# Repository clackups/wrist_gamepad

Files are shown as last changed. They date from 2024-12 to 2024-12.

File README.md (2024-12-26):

# Wrist controlled gamepad

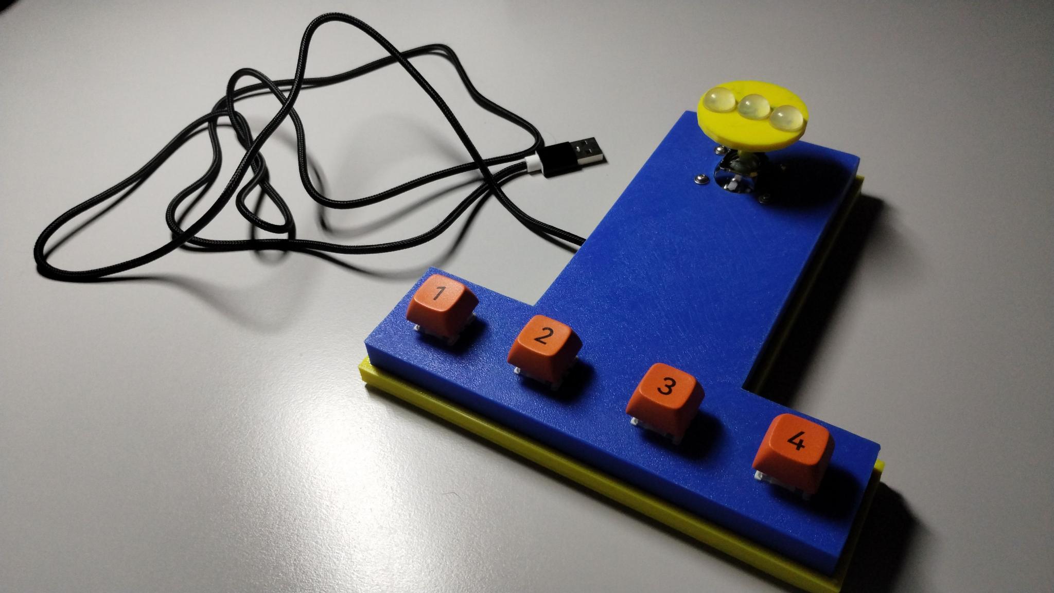
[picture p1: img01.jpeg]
gamepad top view


This is a gamepad I designed for a disabled colleague who cannot bend
his fingers due to a spinal cord injury. The analog joystick is easy to
move with the fingertips, and four buttons can be pressed by the
wrist.

The gamepad runs a copy of [GP2040-CE
firmware](https://gp2040-ce.info/) on an RP2040-Zero board. The four
buttons are wired to GPIO that are mapped by default to buttons
B1..B4, and the joystick push button is mapped to A1. The mapping can
be changed easily in the GP2040 firmware cofiguration. See the
[schematics](wrist_gamepad_schematics.pdf) for reference.

On the bottom of the gamepad, a push-button is wired to the S2
signal. If you press and hold it and plug the USB connector in your
PC, the gamepad starts in configuration mode. You can change the
settings in a browser connected to
[http://192.168.7.1/](http://192.168.7.1/). See the [GP2040
documentation](https://gp2040-ce.info/web-configurator/) for more
details.

The top and bottom parts, as well as the joystick handle are printed
in PLA, 0.2mm layer height, no supports needed. The STL files are
available in [3Dprints](3Dprints/) folder.

Parts list:

* Waveshare RP2040-Zero board. Can also be any other [board supported
  by GP2040-CE firmware](https://gp2040-ce.info/downloads).

* KY-023 Dual Axis Joystick module
  ([1](https://www.amazon.com/dp/B0BPGRN48J),
  [2](https://www.aliexpress.com/item/2251832715984578.html)).

* 4x M2.5*12 screws, 4x M2.5 nuts and 4x M2.5 washers.

* 4x MX keyboard switches, 4 XDA keycaps.

* a small push button for Arduino projects.

* USB-C cable.

* Wires, wire cutter, solderer, soldering iron.

* Hot glue gun (Epoxy would also be suitable).

* Self-adhesive round silicone bumpers (12x6mm for the joystick, 6x2mm
  for the feet).

Once soldered, fixate the keyboard switches and the USB cable with a
hot glue gun, and slide the bottom panel in.

In GP2040-CE web configurator, enable Analog joystick add-on, and map
GP26 to X-axis, and GP27 to Y-axis. Other GPIO pins are already wired
to their default mapping.

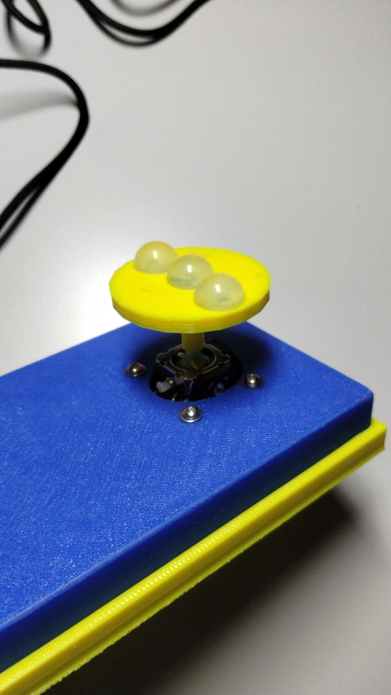
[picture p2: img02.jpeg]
joystick close-up


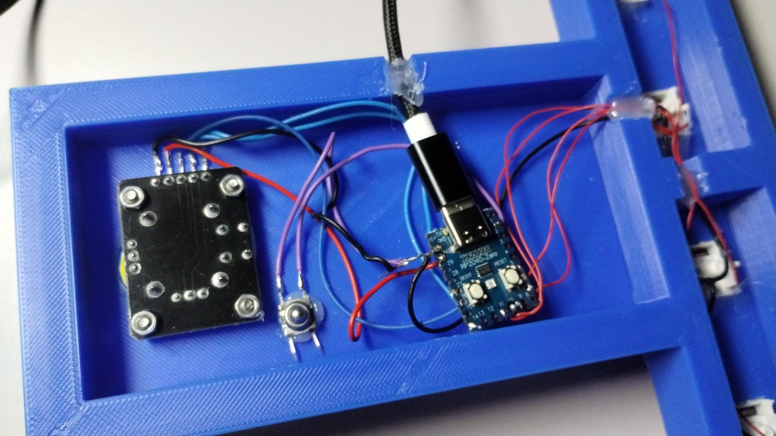
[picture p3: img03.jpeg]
rp2040 and joystick wiring


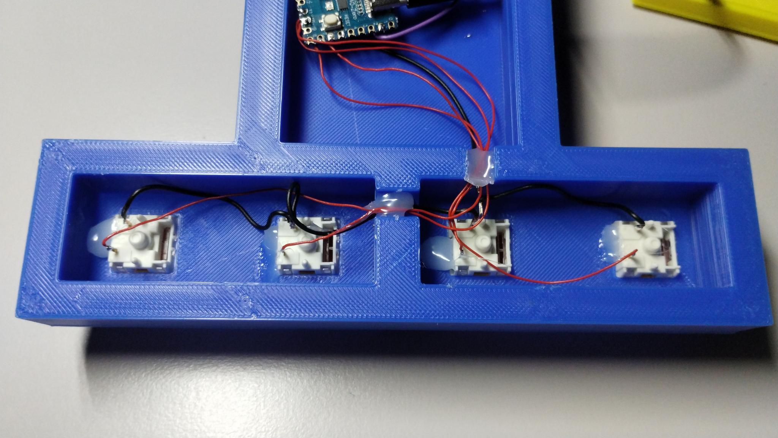
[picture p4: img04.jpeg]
buttons wiring


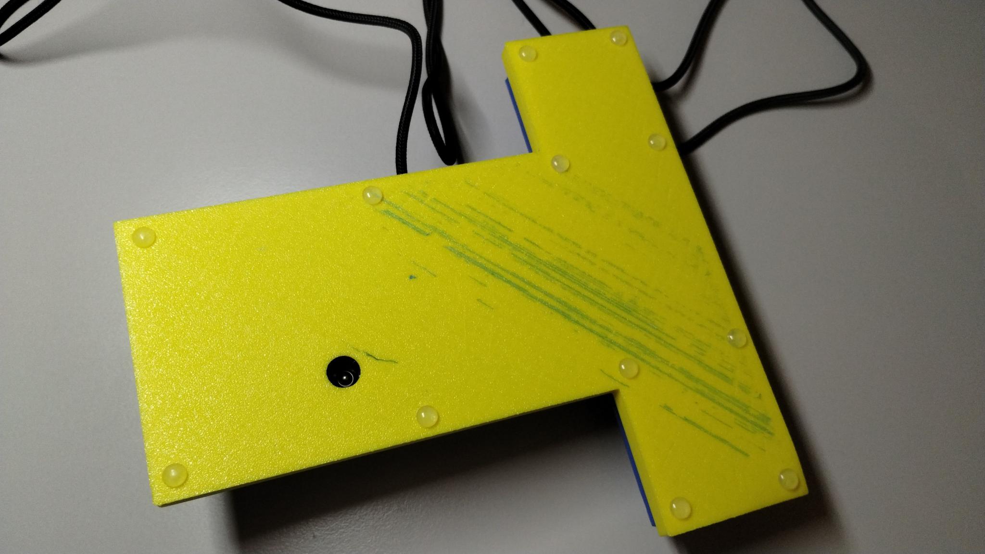
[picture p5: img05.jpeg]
bottom view


## Copyright and license

This work is licensed under Creative Commons
Attribution-NonCommercial-ShareAlike 4.0 International. To view a copy
of this license, visit
https://creativecommons.org/licenses/by-nc-sa/4.0/

Copyright (c) 2024 clackups@gmail.com

Fediverse: [@clackups@social.noleron.com](https://social.noleron.com/@clackups)

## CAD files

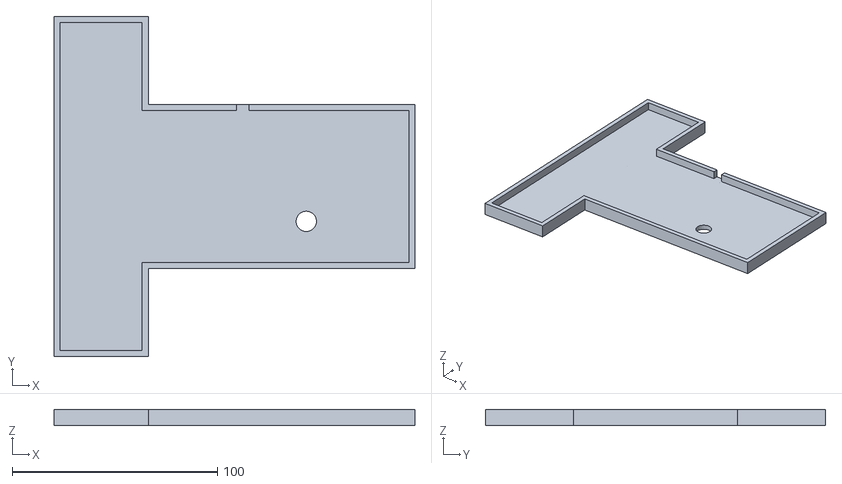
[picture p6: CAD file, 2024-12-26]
3Dprints/bottom_cover_for_wrist_gamepad.stl
176.0 x 166.0 x 8.00

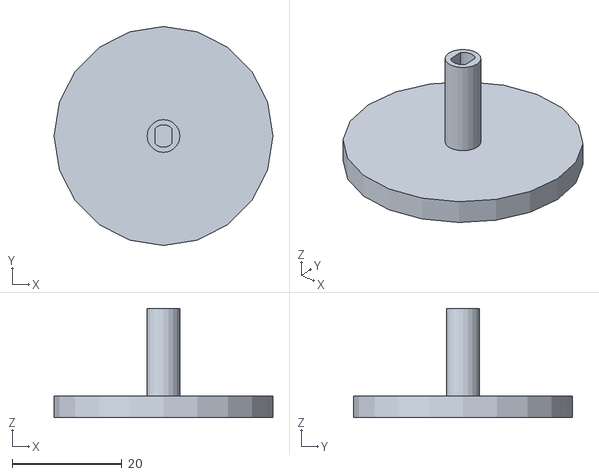
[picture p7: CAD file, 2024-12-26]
3Dprints/joystick_handle.stl
40.0 x 40.0 x 20.0

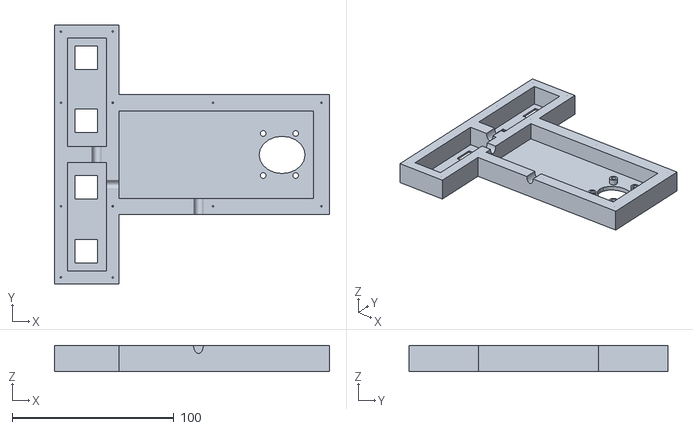
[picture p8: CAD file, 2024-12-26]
3Dprints/wrist_gamepad.stl
170.0 x 160.0 x 16.2

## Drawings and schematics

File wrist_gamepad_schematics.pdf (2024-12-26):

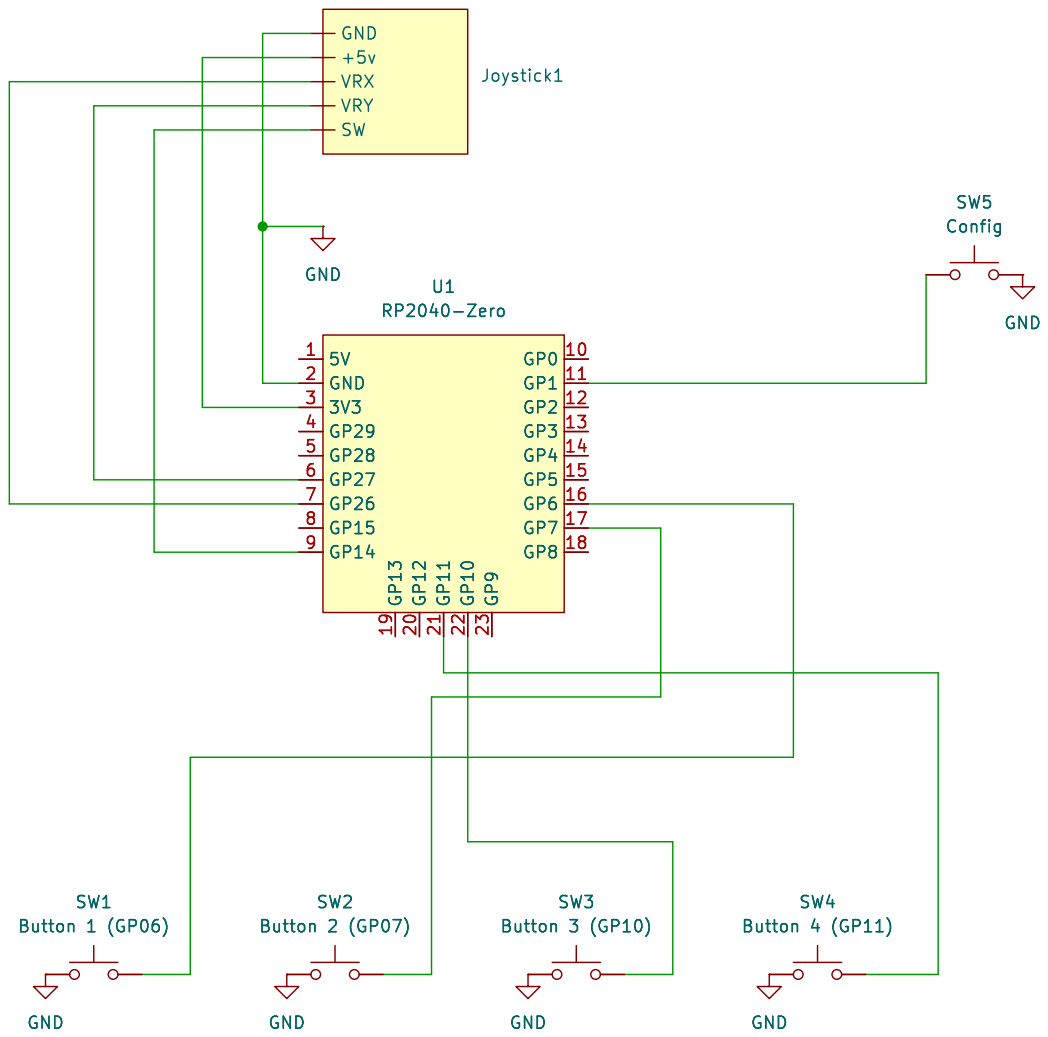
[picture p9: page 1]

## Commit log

2024-12-26 schematics and photos
    [wrist_gamepad.kicad_pcb, wrist_gamepad.kicad_sch]
2024-12-26 description and 3d models
    [bottom_cover_for_wrist_gamepad.stl, joystick_handle.stl, wrist_gamepad.stl]
